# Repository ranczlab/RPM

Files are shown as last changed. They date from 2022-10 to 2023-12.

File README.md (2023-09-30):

# RPM
Documentation files for the Rotation Platform for Mice, as published in Journal of Neuroscience Methods

Read the docs at https://ranczlab.github.io/RPM/

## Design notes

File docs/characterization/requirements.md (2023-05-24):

# Required libraries and software packages

## Software packages
-	[Arduino IDE](https://www.arduino.cc/en/software) 
-	[Teensyduino](https://www.pjrc.com/teensy/teensyduino.html) 

## Required Libraries
-	[Arduino](Arduino/libraries.zip)
-	[ADNS 2160 optical sensor with SQUAL readout](Arduino/libraries.zip) (based on the [OptiMouse library](https://github.com/zapmaker/OptiMouse))
-	[Stepper motor control](https://luni64.github.io/TeensyStep/) 
-	[Encoder](https://github.com/PaulStoffregen/Encoder) 

### Libraries for alternative optical sensors
These are Optical motion sensor options with higher capabilities than the ADNS 2160. All of them use the SPI bus.

-	[ADNS 3500](https://github.com/Tom101222/Adns-3050-Optical-Sensor)
-	[PWM3360](https://github.com/SunjunKim/PMW3360) 
-	[ADNS 9800](https://github.com/mrjohnk/ADNS-9800) 

## Arduino code examples
####[Closed_loop.ino](Arduino/Closed_loop.zip)
The closed loop example uses the optically measured angle increment as a setpoint for the proportional motor control. The animal controls the rotation of the platform.

####[Open_loop.ino](Arduino/Open_loop.zip)
The Open loop example uses two user-defined variables (eg. 0-360 degrees) as setpoints to oscillate between at a user-defined interval.

####[Open_loop_SD.ino](Arduino/Open_loop_SD.zip)
Like the open loop example, but saving the different variables on the SD card on the Teensy 3.5 microcontroller. This program was used to record the accuracy and repeatability measurements.

####[Open_loop_moveAsync.ino](Arduino/Open_loop_moveAsync.zip)
Like Open_loop_SD.ino, but instead of using the proportional control, rotation movement is controlled by the teensystep moveAsync() method, using a non-blocking trapezoidal profile.

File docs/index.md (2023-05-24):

# RPM - a Rotation Platform for head-fixed Mice
## Overview
This device provides vestibular stimulation for head-fixed experiments in mice. It can be combined with different physiological and behavioural recording modalities. It follows a modular, low-cost and open-source model.
This documentation provides the assembly and operation guide for users with some experience in rapid manufacturing, electronics and development boards/microcontrollers, such as Arduino.

In the [accompanying paper](https://www.biorxiv.org/content/10.1101/2023.05.19.541416v1), we show use cases for pupil tracking and recording head-direction cell activity during rotation. 

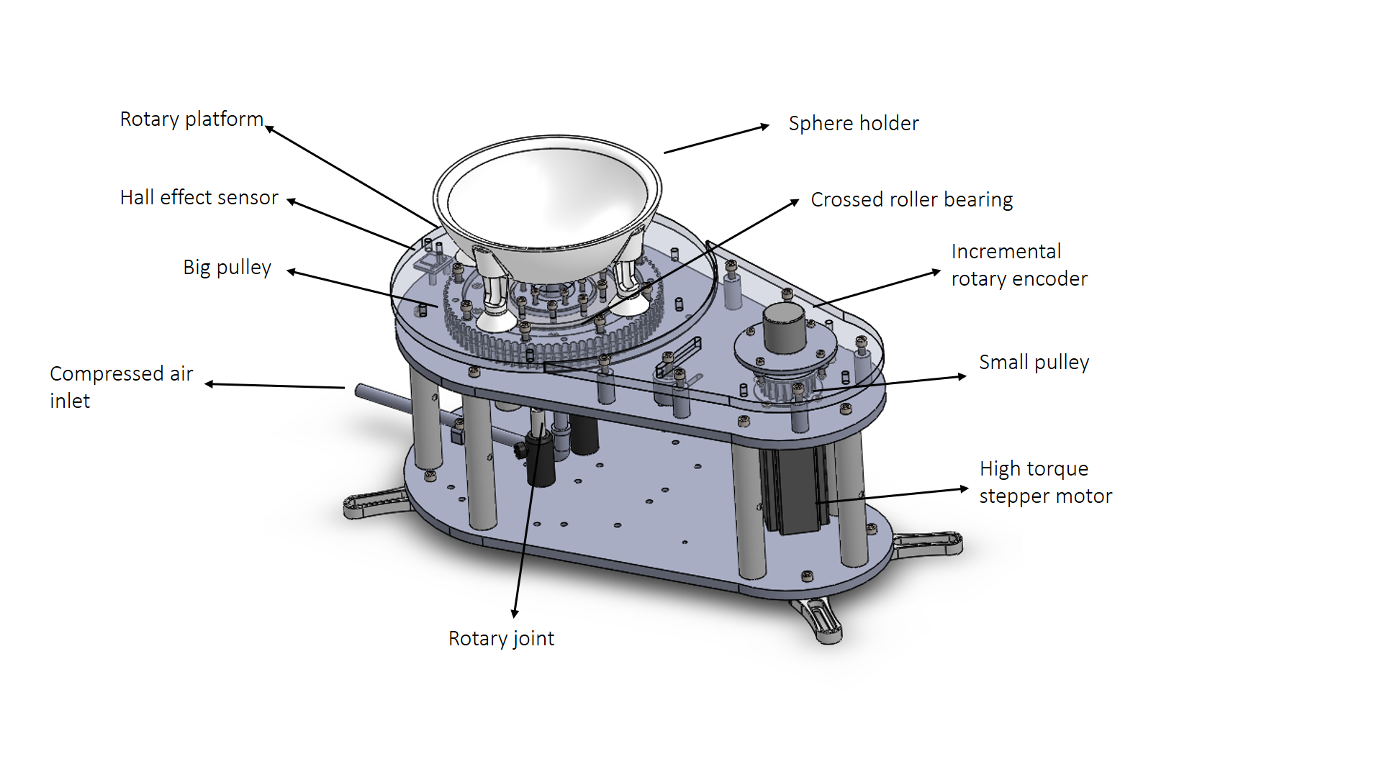
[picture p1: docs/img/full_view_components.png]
|  |
|:--:|
| *Figure 1. Main components of the rotation platform* |
## Features
- fully open source
- low cost
- easy to assemble
- modular design, modules can be added depending on experimental needs

## Main components
The main components of the stage are labelled in the figure above. The rotary platform is actuated by a stepper motor using a timing belt. An incremental encoder is coupled with the motor shaft to measure the angular position, while a Hall effect sensor is used for homing purposes. Compressed air keeps a polystyrene sphere floating without friction inside the sphere holder. The crossed roller bearing holds the rotating and non-rotating parts together. The rotary joint enables multiple electric connections between the rotary platform and the base. The device is intended for behavioural experiments combined with extracellular recording and optogenetics. There are two operating modes: closed-loop and open-loop. In closed-loop mode, the sphere's rotation on the horizontal (yaw) axis is measured using an optical sensor and is used to generate a motor rotation of an adjustable magnitude in the opposite direction. In open-loop mode, motor rotation is independent of the animal’s movement and can be controlled by the experimenter.

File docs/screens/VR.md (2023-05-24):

# Raspberry Pi

The VR environment runs on a Raspberry Pi 4 Modell B located on the platform, running Raspbian 10 (Buster). The Pi is connected to the screens via micro HDMI cables. The Raspberry Pi is powered through one of the USB cables on the slip ring, using a USB to USB-C adaptor. The Teensy USB port is directly connected to one of the USB ports of the Raspberry Pi. Connections are indicated below

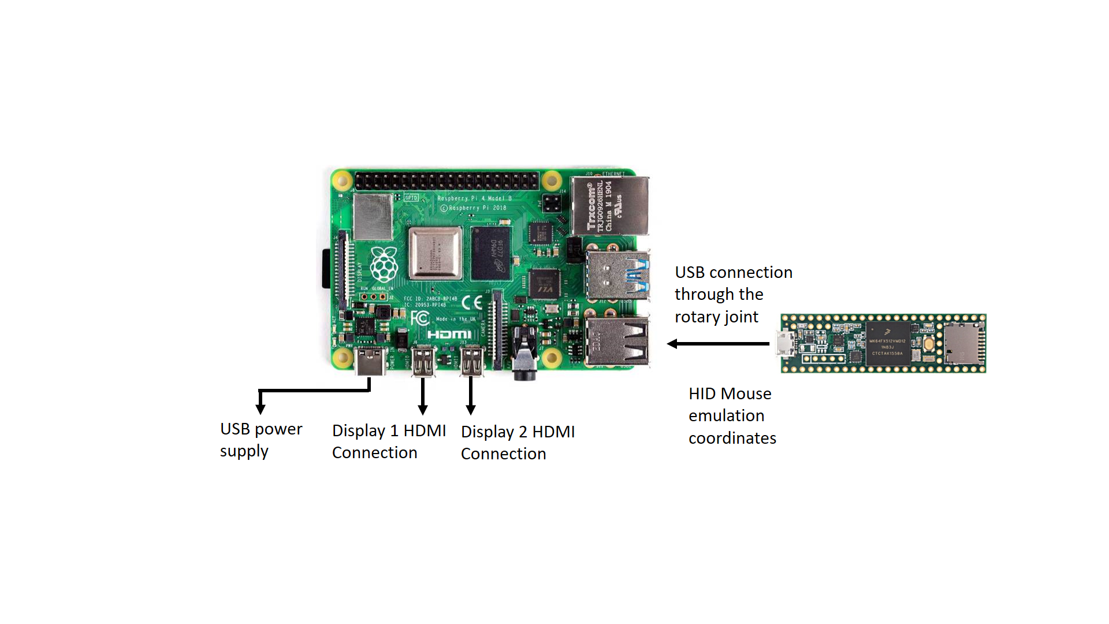
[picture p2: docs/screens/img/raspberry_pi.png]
|  |
|:--:|
| *Figure 1. Connections to Raspberri Pi4* | 
# Sensor input through USB
The optical sensor inputs transformed on the Teensy to calculate the motor displacement are converted using the [Mouse HID Library](https://www.pjrc.com/teensy/td_mouse.html) included in Teensyduino, and transmitted to the Raspberry Pi via USB using the Mouse.move(x, y) function. The Teensy USB port should be set up as a HID + Serial (select the USB mode in Tools -> USB type -> Serial + Keyboard + mouse + joystick when uploading the code using Arduino IDE). 

# Godot

## Compilation instructions
Godot 3.2 is compiled from source using clang. After installing clang and any required libraries (see [here](https://docs.godotengine.org/en/stable/development/compiling/compiling_for_x11.html)), clone and install Godot using the commands below:

```
git clone https://github.com/godotengine/godot
cd godot
git checkout 3.2-stable
scons platform=x11 target=release_debug tools=yes use_llvm=yes CCFLAGS="-mtune=cortex-a72 -mcpu=cortex-a72 -mfloat-abi=hard -mfpu=neon-fp-armv8" -j4
sudo cp bin/godot.x11.opt.tools.32.llvm /usr/bin/godo
```

## Environment

The 3D environment is created in Godot. The camera position is updated using a script written in GDScript, relative to the movements of the emulated mouse carrying the optical sensor input.
The game is run via a bash script that ensures the game is running in full-screen mode across the two monitors.
The (x,y) coordinates of the player within the environment are automatically saved in a csv file. 

The virtual corridor is available [to download here](files/corridor-master.zip)

[The video linked here](https://vimeo.com/829853010) shows a proof-of-principle experiment, where an untrained mouse in navigating on the setup. At the top, a camera behind (and to the right of) the mouse shows the snout, whiskers and the screens. At the bottom, a camera above the setup shows the mouse, the styrofoam ball and the top edge of the screens (helpful to see the physical rotation). The red line in the bottom right shows the trajectory of the animal in VR space.

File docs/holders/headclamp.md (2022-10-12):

## Headplate

The design for the head-plate used with the clamp on the head-holder is shown in Figure 1. 

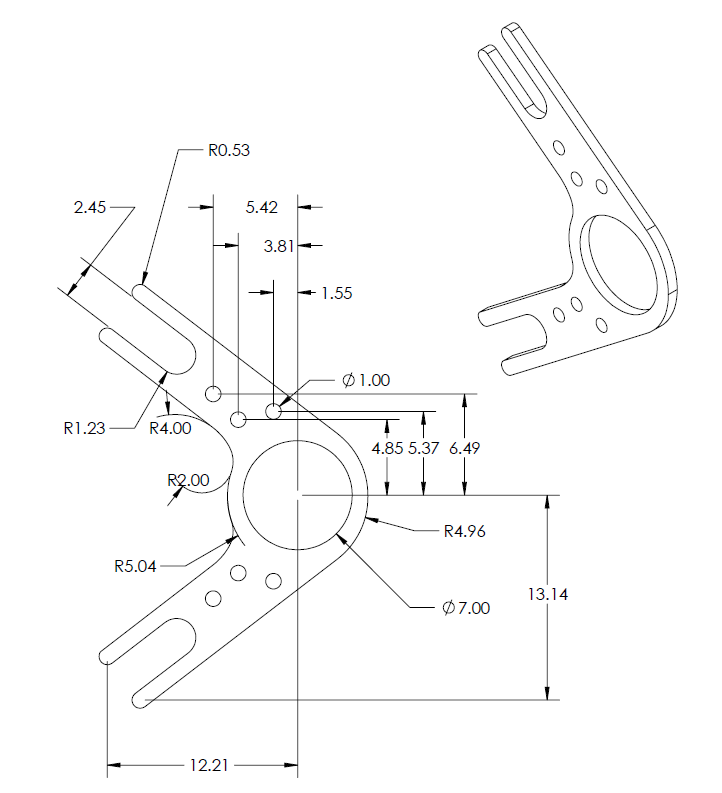
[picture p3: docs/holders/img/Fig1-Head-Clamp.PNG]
|  |
|:--:|
| *Figure 1. Head clamp drawings* |

We have stimulated the performance of the head-plate using different materials (Aluminum, Titanium or Steel) and thicknesses (0.8 mm - 1 mm). The comparison can be performed knowing that the materials will be manufactured using the CNC technique from a block of homogeneous and isotropic material.

The three materials simulated on the Solidworks simulation tool are:

-	Aluminum 6061-T6 1 mm of thickness (0.3g). 
-	Titanium Grade 2 0.8 mm of thickness (0.41g).
-	Stainless steel 316 0.8 mm of thickness (0.73g).

The Initial conditions for the simulation are:

-	A static load applied to the center ring (Blue arrows).
-	Three axis fixture on the parts where the metric 2.5 screws are placed (green arrows).

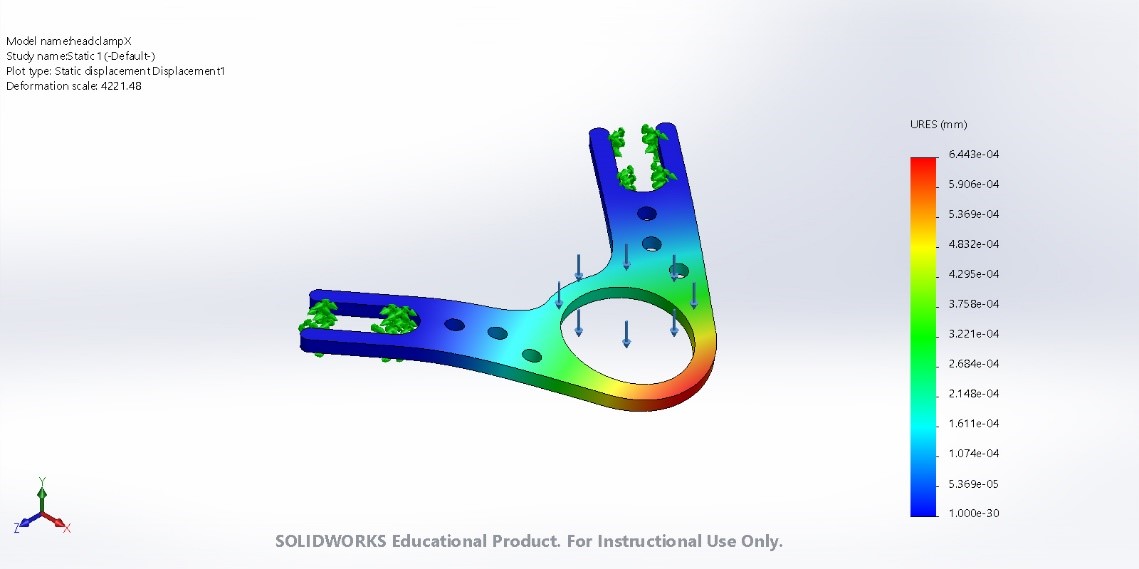
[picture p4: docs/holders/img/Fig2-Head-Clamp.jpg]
|  |
|:--:|
| *Figure 2. Head clamp simulations* |

The results of maximum displacements obtained for each condition

-	Aluminum max. displacement = 9.445e-04 mm
-	Titanium max. displacement = 11.79e-04 mm
-	Stainless Steel max. displacement = 6.443e-04 mm

In conclusion, with the stainless steel head plate of 0.8 mm thickness, the displacement and strain of the head clamp is less than the Aluminum one (1 mm). Otherwise with the Titanium we lose stiffness with 0.8 mm thickness.

Finally, the manufacturing supplier was 3D hubs and the chosen material:

CNC machining / Stainless steel 316L / Smoothed (Ra 1.6μm, 63μin)

The manufacturing files are available [here](files/headclamp/headclampX.IGS) and [here](files/headclamp/headclampX.STL).

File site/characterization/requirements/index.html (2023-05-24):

- Docs »
- Characterization and software »
- Software

# Required libraries and software packages

## Software packages

- Arduino IDE (https://www.arduino.cc/en/software)
- Teensyduino (https://www.pjrc.com/teensy/teensyduino.html)

## Required Libraries

- Arduino
- ADNS 2160 optical sensor with SQUAL readout (based on the OptiMouse library (https://github.com/zapmaker/OptiMouse))
- Stepper motor control (https://luni64.github.io/TeensyStep/)
- Encoder (https://github.com/PaulStoffregen/Encoder)

### Libraries for alternative optical sensors

These are Optical motion sensor options with higher capabilities than the ADNS 2160. All of them use the SPI bus.

- ADNS 3500 (https://github.com/Tom101222/Adns-3050-Optical-Sensor)
- PWM3360 (https://github.com/SunjunKim/PMW3360)
- ADNS 9800 (https://github.com/mrjohnk/ADNS-9800)

## Arduino code examples

#### Closed_loop.ino

The closed loop example uses the optically measured angle increment as a setpoint for the proportional motor control. The animal controls the rotation of the platform.

#### Open_loop.ino

The Open loop example uses two user-defined variables (eg. 0-360 degrees) as setpoints to oscillate between at a user-defined interval.

#### Open_loop_SD.ino

Like the open loop example, but saving the different variables on the SD card on the Teensy 3.5 microcontroller. This program was used to record the accuracy and repeatability measurements.

#### Open_loop_moveAsync.ino

Like Open_loop_SD.ino, but instead of using the proportional control, rotation movement is controlled by the teensystep moveAsync() method, using a non-blocking trapezoidal profile.

Previous

Built with MkDocs (https://www.mkdocs.org/) using a theme (https://github.com/snide/sphinx_rtd_theme) provided by Read the Docs (https://readthedocs.org).

« Previous

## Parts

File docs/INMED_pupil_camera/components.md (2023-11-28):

# Components

Lens
50mm focal length M12 mount lens (CIL051-F2.8-M12ANIR)

M12 Lens extenders
3 x 10 mm per lens 

Camera
FLIR FireFlyS FFY-U3-04S2M-S

## Bill of materials (per screen)
| Component                       | Quantity | Supplier      | Reference                                                  |
|---------------------------------|----------|---------------|------------------------------------------------------------|
| CIL051-F2.8-M12ANIR		 	  | 2       | Commonlands    | [link](https://commonlands.com/products/telephoto-50mm-m12-lens?variant=39733332443254)|
| M12 lens extenders (5 pack)	   	|2         |Amazon|		|[link]https://www.amazon.fr/dp/B0CF9V7S71/ref=pe_27091421_487030221_TE_SCE_3p_dp_1|
| FFY-U3-04S2M-S Camera			|2			|FLIR			|[link]https://www.flir.eu/products/firefly-s/?model=FFY-U3-04S2M-S&vertical=machine+vision&segment=iis|

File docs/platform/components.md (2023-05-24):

# Main components

## Rotary joint

A rotary joint enables electrical communications between the base and the rotating platform. It has a through-hole design for routing the compressed air tube. The selected model is the Senring UH1256-02-0610-06S, of the UH1256-02 Series. It has two USB ports that can be used to connect, e.g. cameras, and several power and data wires to connect different sensors and other accessories.

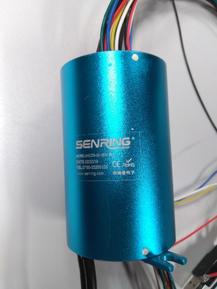
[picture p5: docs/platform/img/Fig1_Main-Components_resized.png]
|  |
|:--:| 
| *Figure 1. Senring UH1256-02-0610-06S Series* |

## Crossed roller bearing

The crossed roller bearing provides a stable joint between the fixed base and the rotation platform. A suitable model for the application is the BRS RU124X considering fitting the rotary joint (inner diameter > 55mm). This bearing provides strong joint stability against axial and radial forces as well as torque due to its best-in-class axial runout (2-5 µm).

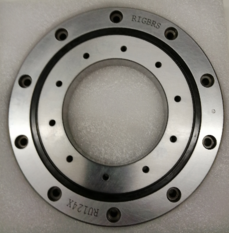
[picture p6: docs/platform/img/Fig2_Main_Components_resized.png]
|  |
|:--:|
| *Figure 2. SBRS RU124X Crossed roller bearing* |

## DC motor and driver
To approximate the motor requirements, we have estimated the moment of inertia around the vertical axis. For this approximation, we have considered two main components: the circular platform and all the elements on the platform and the inner ring of the crossed roller bearing. To simplify the approximation, the internal ring of the bearing has been considered as a stainless steel solid part. The negligible friction force of the bearing has not been taken into account.

Both moments of inertia have been extracted using the mass properties of the Solidworks® CAD software.

equation1

equation2

With this value, we can make the approximation of the torque needed to accelerate the system using Newton’s 2nd law of rotation :
equation3. 

After numerical simulation, we can obtain a theoretical maximum acceleration, useful to choose the motor, described by the function :
equation4

With this relationship, we can estimate the maximum torque needed for the motor. The theoretical maximum angular acceleration is 1100 °/s^2  with a 3 Nm motor option.

A stepper motor was selected accordingly: Nema 23 Stepper Motor 3 Nm 4.2A with a DM542A driver.

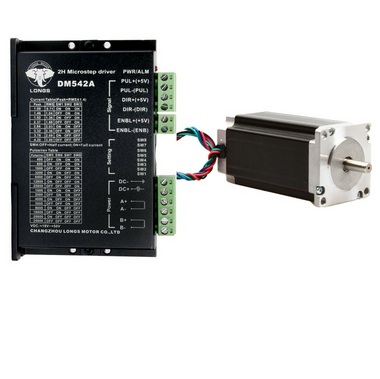
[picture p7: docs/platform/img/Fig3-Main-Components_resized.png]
|  |
|:--:|
| *Figure 3. Nema 23 stepper motor and DM542A stepper driver* |

---
Nema 23 Stepper motor main features:

| Property            	| value 	|
|:---------------------	:|:-------:	|
| steps/rev           	| 200   	|
| L (mH)              	| 3.2   	|
| I<sub>max</sub> (A) 	| 4.2   	|
| V (V)               	| 24    	|
| T (N.m)             	| 3     	|
| P<sub>max</max> (W) 	| 96    	|

---

The current can be selected using the first four switches of the driver DIP switch:
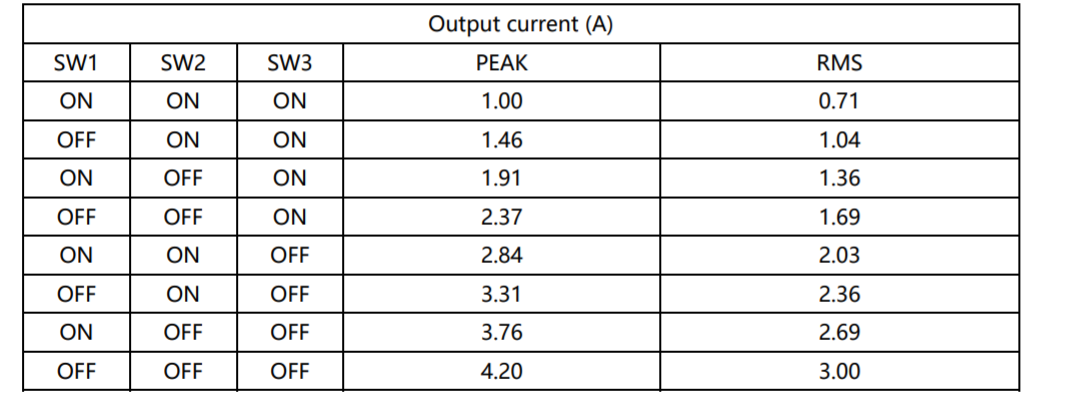
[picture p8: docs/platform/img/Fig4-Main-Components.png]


The driver also has a DIP switch to select the desired micro-stepping mode:
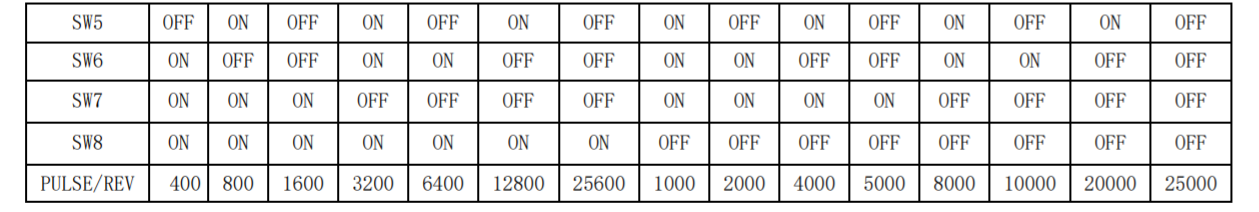
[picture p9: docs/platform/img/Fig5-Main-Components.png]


## Belt selection

We have adjusted the number of teeth zp of the big and the small pulley to get a gear ratio of 6:1 considering the minimum diameter of the big pulley as the outside diameter of the crossed roller bearing BRS RU124X. 

equation11

The diameter of the small (commercially available) pulley with zp = 36 teeth is 34.38 mm. Once the big and small pulley diameters (*D* and *d*) have been defined, the distance between centers (*C*) is calculated to get the desired length *L* :

equation12

The number of teeth obtained for the big pulley is 216, and the distance between centers is 260 mm. These results determined the choice of the belt for our device.
## The timing belt 
The size of the belt was calculated considering the outside diameter of the crossed roller bearing (OD > 165 mm) and the desired gear ratio of 1:6, which provides the stage of a maximum theoretical value of 12 Nm. To calculate the belt parameters, first, we consider the maximum width of the belt for our space constraints, which is 20 mm. According to the distance between centers and the pulley diameters, the required belt length is 927 mm, and the chosen belt width is 15 mm.

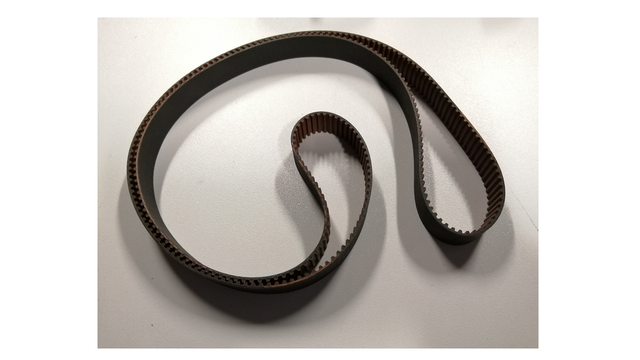
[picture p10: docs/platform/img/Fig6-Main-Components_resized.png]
|  |
|:--:|
| *Figure 6. Timing belt* |

## The small pulley
The pulley driven by the Nema 23 stepper motor is a 36 teeth HTD3 metal pulley provided by RS Components.

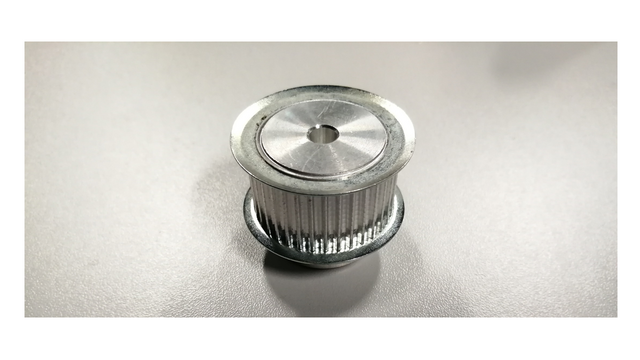
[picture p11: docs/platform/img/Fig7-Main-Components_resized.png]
|  |
|:--:|
| *Figure 7. Small pulley* |

## Bill of materials

3D printing was done using FormLabs Clear V4 resin. PMMA (10 mm thickness) was used for all laser-cut parts unless otherwise indicated.

| Component             	| Quantity 	| Supplier        	| Reference                                                                                                                  |
|-----------------------	|----------	|-----------------	|----------------------------------------------------------------------------------------------------------------------------|
| Resin for 3D printing		|			|					|			|
| Plastic for laser cutting	|			|					|			|
| Base                  	| 1        	| Laser cut		   	| [STEP file](files/STEP/Base.STEP)                                                                                          |
| Platform 2 (Rev1)     	| 1        	| Laser cut 	   	| [STEP file](files/STEP/Platform%202(Rev1).stp)                                                                             |
| Belt cover (Rev1)     	| 1        	| Laser cut 	   	| [STEP file](files/STEP/Belt%20cover(Rev1).stp)                                                                             |
| Circular platform     	| 1        	| Laser cut 	  	| [STEP file](files/STEP/Circular%20rotary%20stage.stp)                                                                      |                                                                                                                                                                                   
| Platform spacer			| 1			| Laser cut			| [STEP file](files/STEP/Spacer.STEP)	|
| Hall-effect sensor spacer | 2         | 3D printed		| [STEP file](files/STEP/Hall%20Effect%20sensor%20spacer.STEP)   															|	
| Hall-effect sensor holder | 1        	| 3D printed 	  	| [STEP file](files/STEP/Hall%20Efect%20sensor%20Holder.stp)                                                                |
| Big pulley (option 1)		| 2			| Laser cut			| [dxf file, layer 1, 5mm thickness](files/dxf/Big pulley%20(1).dxf)|
|							| 1			| Laser cut			| [dxf file, layer 2, 5mm thickness](files/dxf/Big pulley%20(2).dxf)|
|							| 2			| Laser cut			| [dxf file, layer 2, 3mm thickness](files/dxf/Big pulley%20(2).dxf)|
|							| 1			| Laser cut			| [dxf file, layer 3, 3mm thickness](files/dxf/Big pulley%20(3).dxf)|
| Big pulley (option 2, Rev1)     	|         	| 3D printed 	  	| [STEP file](files/STEP/Big%20pulley%20(Rev1).stp), [STL file](files/STL/Big%20pulley%20(Rev1).stl) |                                                                                                                                                                                                        
| Belt tensor           	| 1        	| 3D printed        | [STEP file](files/STEP/Belt%20tensor.STEP) | 
| Encoder holder        	| 1        	| Laser cut 	  	| [STEP file, 5mm thickness](files/STEP/Encoder%20holder.STEP)  |
| Encoder spacer        	| 4        	| Laser cut / 3D printed     | [STEP file, 5mm thickness](files/STEP/Encoder%20spacer.STEP) 	|
| Encoder attachment     	| 1        	| 3D printed      	| [STEP file](files/STEP/Encoder%20attachment.stp), [STL file](files/STL/Encoder%20attachment.stl)     |
| Cover spacer          	| 6        	| 3D printed       	| [STEP file](files/STEP/Cover%20spacer.STEP)  |
| Tube guide            	| 1        	| 3D printed      	| [STEP file](files/STEP/Tube%20guide.STEP)   |
| Rotary joint spacer   	| 1        	| 3D printed     	| [STEP file](files/STEP/Rotary%20joint%20spacer.STEP) |
| Sphere holder   			| 1        	| 3D printed    	| [STL file](files/STL/Sphere%20Holder.STL)       |
| Small pulley (Rev1)   	| 1        	| RS Components 	| [link](https://uk.rs-online.com/web/p/belt-pulleys/1465412/)  |
| Belt                  	| 1        	| Ebay            	| [link](https://www.ebay.co.uk/itm/324243196114)     |
| CF175                 	| 4        	| Thorlabs        	| [link](https://www.thorlabs.com/thorproduct.cfm?partnumber=CF175)    |
| RS05P 				  	| 4        	| Thorlabs        	| [link](https://www.thorlabs.com/thorproduct.cfm?partnumber=RS05P/M)  |
| RS150                 	| 7        	| Thorlabs        	| [link](https://www.thorlabs.com/thorproduct.cfm?partnumber=RS150/M)  |
| TR_50M                	| 2     	| Thorlabs        	| [link](https://www.thorlabs.com/thorproduct.cfm?partnumber=TR50/M)   |
| PH_50                 	| 2        	| Thorlabs        	| [link](https://www.thorlabs.com/thorproduct.cfm?partnumber=PH50/M)    |
| M6 washers            	| 2        	| Thorlabs        	| [link](https://www.thorlabs.com/newgrouppage9.cfm?objectgroup_id=248) |
| M6 screws             	| 44       	| Thorlabs        	| [link](https://www.thorlabs.com/newgrouppage9.cfm?objectgroup_id=248) |
| M5 screws             	| 24       	| Thorlabs        	| [link](https://www.thorlabs.com/newgrouppage9.cfm?objectgroup_id=248) |
| M4 screws             	| 11       	| Thorlabs        	| [link](https://www.thorlabs.com/newgrouppage9.cfm?objectgroup_id=248) |
| M3 screws             	| 7        	| Thorlabs        	| [link](https://www.thorlabs.com/newgrouppage9.cfm?objectgroup_id=248)  |
| M3 grub screw (25mm)		|			| Amazon			| [link](https://www.amazon.co.uk/25mm-Socket-Grub-Screw-Point/dp/B07SJ7XDKB)					|
| M6 nuts               	| 9        	| Thorlabs         	| [link](https://www.thorlabs.com/newgrouppage9.cfm?objectgroup_id=248)  |
| M5 nuts               	| 14       	| Thorlabs       	| [link](https://www.thorlabs.com/newgrouppage9.cfm?objectgroup_id=248)   |
| BRS RU124X bearing    	| 1        	| BRS             	| [link](http://www.rigbrsbearing.com/product/ru124x-cross-roller-ring/)   |
| Rotary Joint          	| 1        	| Senring         	| [link](https://www.senring.com/usb-conductive-slip-ring/dual-Channels/uh1256-02.html)  |
| Encoder               	| 1        	| Amazon          	| [link](https://www.amazon.co.uk/Incremental-Encoder-2-Phases-Photoelectric-Supplies/dp/B085774B2G) |
| Hall effect sensor     	| 1        	| Amazon          	| [link](https://www.amazon.co.uk/AZDelivery-KY-003-Hall-Sensor-Parent/dp/B081B47VM1) |
| Magnet                	| 1        	| RS Components 	| [link](https://uk.rs-online.com/web/p/neodymium-magnets/7924559)  |
| Nema 23 motor & driver 	| 1        	| Ebay            	| [link](https://www.ebay.co.uk/itm/Free-Ship-Nema-23-Stepper-Motor-435oz-in-4-2A-Driver-Controller-DM542A/273805042516) |
| M6 threaded insert    	|          	| RS Components     | [link](https://uk.rs-online.com/web/p/threaded-inserts/6647359)      |
| M4 threaded insert	   	|          	| RS Components   	| [link](https://uk.rs-online.com/web/p/threaded-inserts/0278556)       |
| M3 threaded insert   		|          	| RS Components   	| [link](https://uk.rs-online.com/web/p/threaded-inserts/0278534)     															|
| Bearings              	| 2        	| RS Components 	| [link](https://uk.rs-online.com/web/p/neodymium-magnets/6190014) |
| Pneumatic tube 			| 1			| Amazon			| [link](https://www.amazon.co.uk/ERGAOBOY-Blue-Polyurethane-Pneumatic-Connector/dp/B0BYHPLCDT/)		|
| Pneumatic tube joint		| 1			| Amazon 			| [link](https://www.amazon.co.uk/Pneumatic-Connector-10Pcs-Fittings-Connectors/dp/B095RVTGTG)		|

## Datasheets and documents

| Component             	| Reference                                                                                                                |
|-----------------------	|--------------------------------------------------------------------------------------------------------------------------|
| BRS RU124X bearing	   	| [Datasheet](Datasheets%20and%20documents/Crossed%20roller%20bearing/RU-crossed-roller-bearing-BRS-Bearing.pdf)           |
| 						   	| [Inspection Report](Datasheets%20and%20documents/Crossed%20roller%20bearing/RU124X-Inspection%20Report-BRS Bearing.pdf)  |
| Nema 23 motor & driver 	| [Datasheet](Datasheets%20and%20documents/Motor%20and%20Driver/Nema23_eBay.pdf)		|
| Rotary joint 				| [Datasheet](Datasheets%20and%20documents/Slipring-Rotary%20Joint/Senring-UH1256-01-Series-SlipRing-Catalog.pdf)		|

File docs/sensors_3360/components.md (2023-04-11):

# Components

The PMW3360 has exceptional capabilities: high motion detection for speeds up to 635 cm/s and acceleration up to 50G. The register outputs the SQUAL value, a reference of the quality of the surface. The sensor is available for purchase from JACK Enterprises in Tindie [[1]](#references). To control it you must download the PWM3360 library [[2]](#references). 

The breakout board has the essential pins available and distributed in a way that makes it easy to connect:

- VI = 3.3V
- MI = MISO0 -or- DIN
- MO = MOSI0 -or- DOUT
- SC = SCK0 -or- SCK
- SS = CS0 -or- CS
- GD = GND

The holder can be 3D printed ([STL file](files/STL/PWM3360%20holder.stl) and [STP file](files/STP/PWM3360%20holder.stp)) and be used with the Thorlabs parts described for the other sensors (ADNS 2610 and 3050). To attach the sensor to the holder, two M2.5 16 mm pan head screws and two M2.5 nuts are needed. The nuts can be pressed to fit on the holder, and the bolts will hold the lens against the sensor without needing glue (Figure 1).

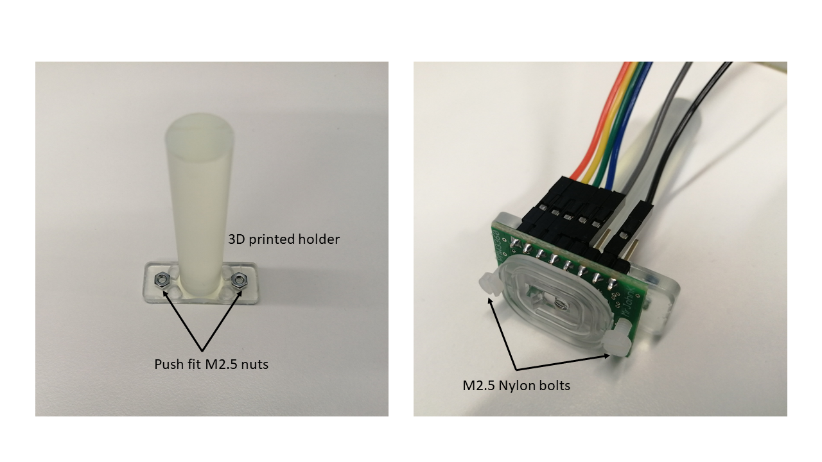
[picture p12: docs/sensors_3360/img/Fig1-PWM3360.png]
|  |
|:--:|
| *Figure 1. 3D printed holder and assembly* |

# References
[1] [https://www.tindie.com/products/jkicklighter/pmw3360-motion-sensor/](https://www.tindie.com/products/jkicklighter/pmw3360-motion-sensor/)

[2] [https://github.com/SunjunKim/PMW3360](https://github.com/SunjunKim/PMW3360)

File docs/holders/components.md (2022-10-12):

## Instrument ring

A ring-shaped instrument platform can be mounted around the sphere to hold several devices, such as an animal head-holder, cameras, and manipulators for electrical recording and optogenetic stimulation. Below we present options for head-clamps and holders for manipulating recording probes or optical fibres.

|  |
|:--:|
| *Figure 1. Ring platform and head holding system* |

## Head-plate holder

We designed a head fixation system with three degrees of freedom. The height of the head-plate holder can be adjusted to accommodate mice of different sizes. In addition, two orthogonal axes are used in the horizontal plane to adjust the position of the animal's head. This is particularly useful for vestibular experiments to centre the platform rotation axis on the vestibular organ of interest. 

This head holding system is based on assembling 3 manual Thorlabs translational stages (MT1\M) to ensure reliability and repeatability across experiments. The resolution of the system is 10 microns with a range of 13 mm in all directions.

|  |
|:--:|
| *Figure 2. Virtual assembly of the head post (left) and real assembly (right).* |

The materials needed for the assembly are: 3D printable parts (MT1/M linker, Head plate holder 1), the three MT1\M translational stages, three MT405 side mounted actuator adapters, two M2.5 nuts, two hexagonal M2.5 screws, fifteen M6 screws (two of them optional) and two M6 threaded inserts (optional). 

|  |
|:--:|
| *Figure 3. Drawings of the MT1/M linker at 1:2 scale* |

We also provide an MT1/M linker with a side-lip useable for attaching e.g. a camera or another instrument. 
An alternative Head-plate holder 2 is provided for attaching an MM33 manual micromanipulator. 

## Probe holder and optic fibre holder

A probe holder is provided for attaching e.g. a Neuronexus adaptor (Adpt-A32-OM32) to the MM33 micromanipulator for electrophysiological recordings.

For optogenetic stimulation, an optic fibre can be secured to the MM33 micromanipulator using the Thorlabs FCM13/M ferrule clamp and a custom 3D printed adaptor. This allows the positioning of the light source at the desired location over the animal's head.

|  |
|:--:|
| *Figure 6. Optical fiber holder* |

## Bill of materials
The 3D printed parts have been printed using a Form2 SLS 3D printer using the default settings with Clear V4 resin type.

| Component                           | Manufacturer    | Units           | Reference             |
|-------------------------------------|-----------------|-----------------|-----------------------|
| Instrument ring                     | 3D printed 		| 1               | [STP file](files/STEP/Ring.stp), [STL files](files/STL/Ring.stl)        |
| MT1/M linker						  | 3D printed 		| 1               | [STP file](files/STEP/linkMT1_M.stp)|
| MT1/M linker with camera holder lip | 3D printed 		| 1               | [STP file](files/STEP/linkMT1_M_camera%20modification.STEP), [STL files](files/STL/linkMT1_M_camera%20modification.STL)        |
| Head-plate holder 1				  | 3D printed		| 1				  |	[STP file](files/STEP/Head_plate_holder_1.stp)				|
| Head-plate holder 2 (for MM33 manipulator)            | 3D printed	  | 1               | [STP file](files/STEP/Head_plate_holder_2.stp), [STL file](files/STL/Head_plate_holder_2.stl)        |
| Probe holder                  	  | 3D printed 		| 1               | [STP file](files/STEP/Neuronexus%20holder.stp) |
| Optic fiber holder                  | 3D printed 		| 1               | [STP file](files/STEP/Optic%20fiber%20holder.stp), [STL file](files/STL/Optic%20fiber%20holder.stl) |
| MT1/M translational stage           | Thorlabs        | 3               | [link](https://www.thorlabs.com/thorproduct.cfm?partnumber=MT1/M#ad-image-0)                 |
| MT405 side mounted actuator adapter | Thorlabs        | 3               | [link](https://www.thorlabs.com/newgrouppage9.cfm?objectgroup_id=1908&pn=MT405#1929)                 |
| RS6P/M posts						  | Thorlabs		| 2				  | [link](https://www.thorlabs.com/newgrouppage9.cfm?objectgroup_id=851&pn=RS6P/M#1307)|
| M6 hex bold screws 16mm length      | RS components   | 15 (2 optional) | [link](https://uk.rs-online.com/web/p/socket-screws/0281114)               |
| M2.5 hex bold screws                | RS components   | 4               | [link](https://uk.rs-online.com/web/p/socket-screws/4838124)      |
| M2.5 nuts                           | RS components   | 2               | [link](https://uk.rs-online.com/web/p/hex-nuts/0560287)               |
| M6 threaded inserts                 | RS components   | 2 (optional)    | [link](https://uk.rs-online.com/web/p/threaded-inserts/6647359)              |
| M4 screws                           |                 | 3               |                       |
| M3 screws                           |                 | 2               |                       |
| Optic fibre holder (FCM ferrule clamp)				  | Thorlabs		| 1				  | [link](https://www.thorlabs.com/newgrouppage9.cfm?objectgroup_id=69)
| Left handed MM33 micromanipulator   | Märzhäuser      | 1               |[link](https://www.marzhauser.com/en/products/micromanipulators/manual-micromanipulators/mm-33.html), [datasheet](files/Datasheets/Micromanipulator/00-42-101-0000_MM_33_EN.pdf)|

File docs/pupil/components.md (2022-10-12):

# Camera-mirror complex for pupil tracking

A camera can be added to the ring-shaped instrument platform to record e.g. eye or facial movements. We chose a web camera with a small footprint, low weight and USB connectivity through the rotary joint. It lacks an IR filter. We used an IR LED for illumination and a Thorlabs FEL0750 - Ø1" long pass filter mounted on a CP35/M - 30 mm cage Plate using an SM1L03 lens tube. 

The image of the animal is reflected on an FM02R red hot mirror ((25 mm x 36 mm) with an incidence angle of 45°. The mirror position can be adjusted with Thorlabs post elements, and the camera can be rotated and translated for adequate positioning.

|  |
|:--:|
| *Figure 1. Camera with hot mirror* | 

## Bill of materials

| Component                            	| Quantity 	| Supplier 	| Reference                                                                                      	|
|--------------------------------------	|----------	|----------	|------------------------------------------------------------------------------------------------	|
| Mirror holder                        	| 1        	| 3D   printed        	|[STP file](files/STEP/Mirror%20holder.STEP), [STL file](files/STL/Mirror%20holder.STL)                                                                              	|
| Camera holder                        	| 1        	| 3D   printed        	|[STP file](files/STEP/Camera%20holder.STEP), [STL file](files/STL/Camera%20holder.STL)                                                                              	|
| Filter holder                        	| 1        	| 3D   printed        	|[STP file](files/STEP/Filter%20holder.STEP), [STL file](files/STL/Filter%20holder.STL)                                                                              	|
| Filter holder cover                  	| 1        	| 3D   printed        	|[STP file](files/STEP/Filter%20holder%20cover.STEP), [STL file](files/STL/Filter%20holder%20cover.STL)                                                                              	|
| M2 screw                             	| 4        	| -        	| -                                                                                              	|
| M3 screw                             	| 6        	| -        	| -                                                                                              	|
| M2 nuts                              	| 4        	| -        	| -                                                                                              	|
| M6 screw                             	| 1        	| -        	| -                                                                                              	|
| M6 nut                               	| 1        	| -        	| -                                                                                              	|
| FEL0750 - Ø1" Long pass Filter       	| 1        	| Thorlabs 	| [link](https://www.thorlabs.de/thorproduct.cfm?partnumber=FEL0750)                                     	|
| CP35/M - 30 mm Cage Plate            	| 1        	| Thorlabs 	| [link](https://www.thorlabs.com/thorproduct.cfm?partnumber=CP35/M)                                     	|
| SM1L03 - SM1 Lens Tube               	| 1        	| Thorlabs 	| [link](https://www.thorlabs.com/thorproduct.cfm?partnumber=SM1L03)                                     	|
| FM02R - 25 mm x 36 mm Red Hot Mirror 	| 1        	| Thorlabs 	| [link](https://www.thorlabs.com/thorproduct.cfm?partnumber=FM02R)                                      	|
| ELP webcam 				         	| 1        	| Amazon   	| [link](https://www.amazon.co.uk/gp/product/B015PCAVZG) 	|

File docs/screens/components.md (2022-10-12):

# Components

Two 8” SKD819VAHT-9 TFT displays are attached to the rotary platform using two Thorlabs RS6P_M posts. The displays are attached to the posts with a 3D printed part (Screen attachment 1). The display frame comprises three laser-cut acrylic parts and some laser-cut spacers. Eight M4 screws and nuts are required to build the acrylic structure, and an M6 screw is required to attach the 3D printed attachment with the Thorlabs post.

## Bill of materials (per screen)
| Component                       | Quantity | Supplier      | Reference                                                  |
|---------------------------------|----------|---------------|------------------------------------------------------------|
| SKD819VAHT-9 TFT screens		  | 1        | -             | [link](https://www.alibaba.com/product-detail/SKD819VAHT-9-HDMI-Input-Touch-screen_1600192797730.html)                                               |
| Screen holder front             | 1        | Laser cut              | [STP file](files/STEP/Screen%20holder%20front.stp), [DXF file](files/DXF/Screen%20holder%20front.dxf)                                             |
| Screen holder back              | 1        | Laser cut              | [STP file](files/STEP/Screen%20holder%20Back.stp), [DXF file](files/DXF/Screen%20holder%20back.dxf)                                             |
| Screen holder back 2            | 1        | Laser cut              | [STP file](files/STEP/Screen%20holder%20Back%202.stp), [DXF file](files/DXF/Screen%20holder%20back%202.dxf)                                             |
| Screen attachment 1             | 1        | 3D printed              | [STP file](files/STEP/Screen%20attachment%201.stp), [STL file](files/STL/Screen%20attachment%201.stl)                                            |
| Spacer                          | 4        | 3D printed              | [STP file](files/STEP/Spacer.stp), [STL file](files/STL/Spacer.stl)                                            |
| Spacer 2                        | 4        | 3D printed              | [STP file](files/STEP/Spacer%202.stp), [STL file](files/STL/Spacer%202.stl)                                            |
| RS6P/M                          | 1        | Thorlabs      | [link](https://www.thorlabs.com/thorproduct.cfm?partnumber=RS6P/M) |
| M4 screw                        | 8        | RS Components | [link](https://uk.rs-online.com/web/p/socket-screws/0281057/)      |
| M4 nut                          | 4        | RS Components | [link](https://uk.rs-online.com/web/p/hex-nuts/0189579/)           |
| M6 screw                        | 1        | RS Components | [link](https://uk.rs-online.com/web/p/socket-screws/8741030/)      |

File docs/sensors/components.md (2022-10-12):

# Optical motion sensors

## Sensors

To measure the position of the sphere, we used two PCB boards based on the Avago Technologies ADNS-2610 [[1]](#references) optical flow sensor and extracted from the Logitech M-SBF96 PS2 computer mouse. This sensor presents high reliability for speeds under 30.5 cm/s, and has a register that outputs the SQUAL value, a reference for the quality of the surface. This SQUAL value can be used for calibration and optimization. 

|  |
|:--:|
| *Figure 1. Pinout of the ADNS-2610* |

The PCB and lens are attached to a 3D printable structure and assembled with 3 Thorlabs components.

|  |
|:--:|
| *Figure 2. Optical sensor* |

## Bill of materials (per sensor)

The 3D-printed parts have been designed to be printed optimally with an Objet 30 (Polyjet resin printer), but have also been printed with a Form 2 (SLS resin printer). We used the Vero gray resin and the Clear V4 resin with the Objet 30 and the Form 2 respectively. Printer settings were kept at default.

| Component          | Quantity | Supplier      | Reference                                                                                               |
|--------------------|----------|---------------|-----------------------------------------------------------------------------------------------------------|
| Optical mouse      | 1        | -             | [example link](https://www.ebay.com/itm/232746871340) |
| Sensor holder      | 1        | 3D printed    | [STEP file](files/Sensor%20holder.stp), [STL file](files/Sensor%20holder.stl)                            |
| PH75/M             | 1        | Thorlabs      | [link](https://www.thorlabs.com/thorproduct.cfm?partnumber=PH75/M)                                           |
| RA180/M            | 1        | Thorlabs      | [link](https://www.thorlabs.com/newgrouppage9.cfm?objectgroup_id=1985&pn=RA180#6066)                        |
| TR75V/M            | 1        | Thorlabs      | [link](https://www.thorlabs.com/newgrouppage9.cfm?objectgroup_id=1266&pn=TR75V/M#7832)               |
| M3 x 6 mm          | 2        | RS Components | [link](https://uk.rs-online.com/web/p/grub-screws/0137720)                                             |
| M3 threaded insert | 2        | RS Components | [link](https://uk.rs-online.com/web/p/threaded-inserts/0278534)                                       |

# References

[1] [ADNS-2610 datasheet](datasheets/ADNS-2610.pdf)

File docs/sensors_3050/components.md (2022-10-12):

# Optical motion sensors - option 2, ADNS-3050

## Sensors

Another option to measure the sphere's position is to use two PCB boards based on the Avago Technologies ADNS-3050 optical flow sensor. The sensor was extracted from the Cougar Minos X2 gaming computer mouse. This sensor has high motion detection under speeds of 152.4 cm/s and can deal with accelerations up to 20G. It has selectable resolutions up to 2000 cpi (we have used the default configuration of 1000 cpi). Furthermore, the register outputs the SQUAL value, which is used for the calibration and adjustment process.

|  |
|:--:|
| *Figure 1. Pinout of the ADNS-3050* |

## Bill of materials (per sensor)
| Component          | Quantity | Supplier      | Reference                                                                                                                                               |
|--------------------|----------|---------------|---------------------------------------------------------------------------------------------------------------------------------------------------------|
| Optical mouse      | 1        | -             | [link](https://cougargaming.com/products/mice/minos_x2/)|
| PCB Holder 1     | 1        | 3D printed part             | [STEP file](files/STEP/PCB%20holder.STEP), [STL file](files/STL/PCB%20holder.STL) |
| PCB Holder 2    | 1        | 3D printed part             | [STEP file](files/STEP/PCB%20holder%202.STEP), [STL file](files/STL/PCB%20holder%202.STL) |
| M3 screws       | 4        | RS Components               |                                                                             |

The rest of the components are the same as described in the ADNS 2610 assembly.

# Datasheets
[1] [ADNS-3050 datasheet](datasheets/adns-3050.pdf)

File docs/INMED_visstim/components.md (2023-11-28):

# Components

Visual stimuli used for experiments 

1. Motion Clouds 
Based on [link]https://neuralensemble.org/MotionClouds/index.html

## Bill of materials (per screen)
| Component                       | Quantity | Supplier      | Reference                                                  |
|---------------------------------|----------|---------------|------------------------------------------------------------|
| example		 				  | 1        | -             | [link](https://www.alibaba.com/product-detail/SKD819VAHT-9-HDMI-Input-Touch-screen_1600192797730.html)

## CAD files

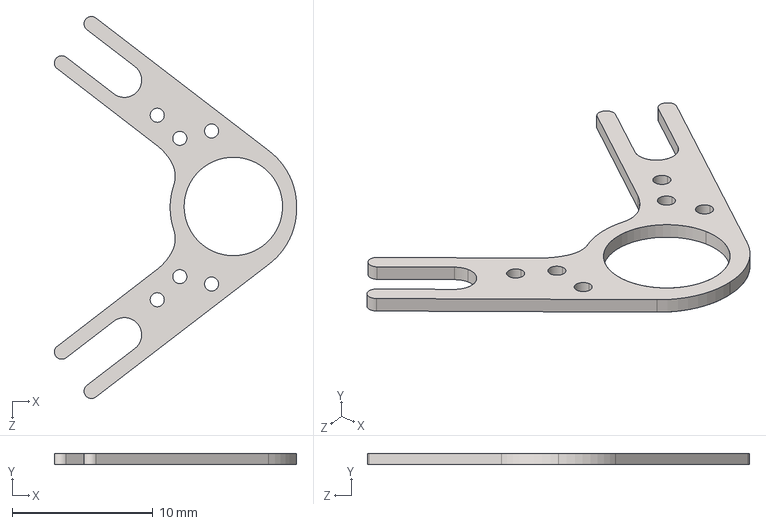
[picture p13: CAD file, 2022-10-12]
docs/holders/files/headclamp/headclampX.IGS
17.2 x 0.8 x 27.2 mm

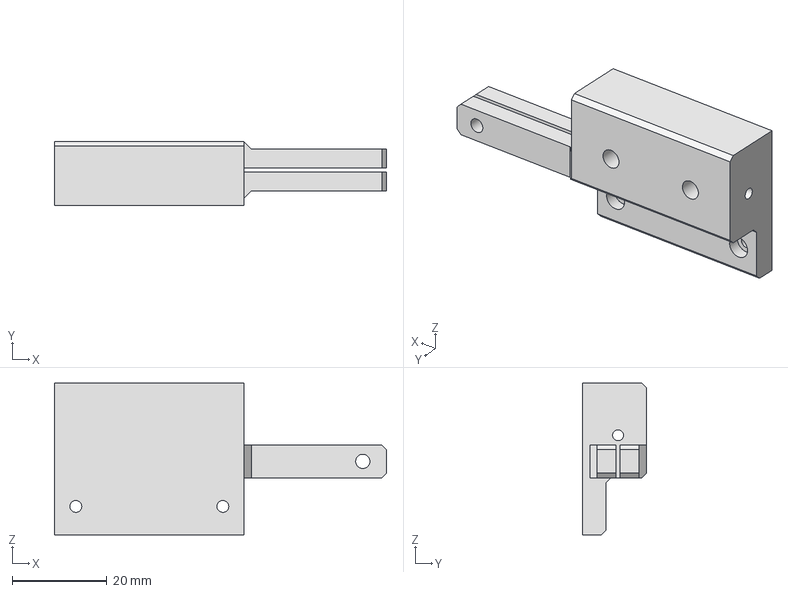
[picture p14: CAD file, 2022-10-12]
docs/holders/files/STEP/Neuronexus holder.stp
70.0 x 13.5 x 32.0 mm

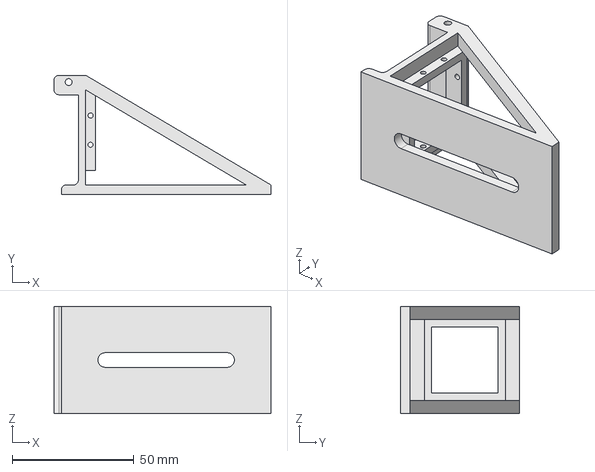
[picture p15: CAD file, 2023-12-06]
docs/INMED_camera_holder/STEP/camera_holder_new.step
89.0 x 49.0 x 44.0 mm

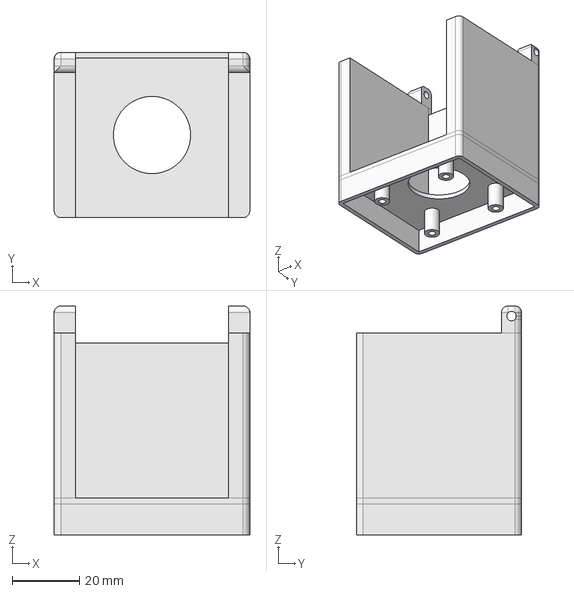
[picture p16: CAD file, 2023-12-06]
docs/INMED_filter_holder/STEP/filter_holder_new.step
58.0 x 49.0 x 67.9 mm

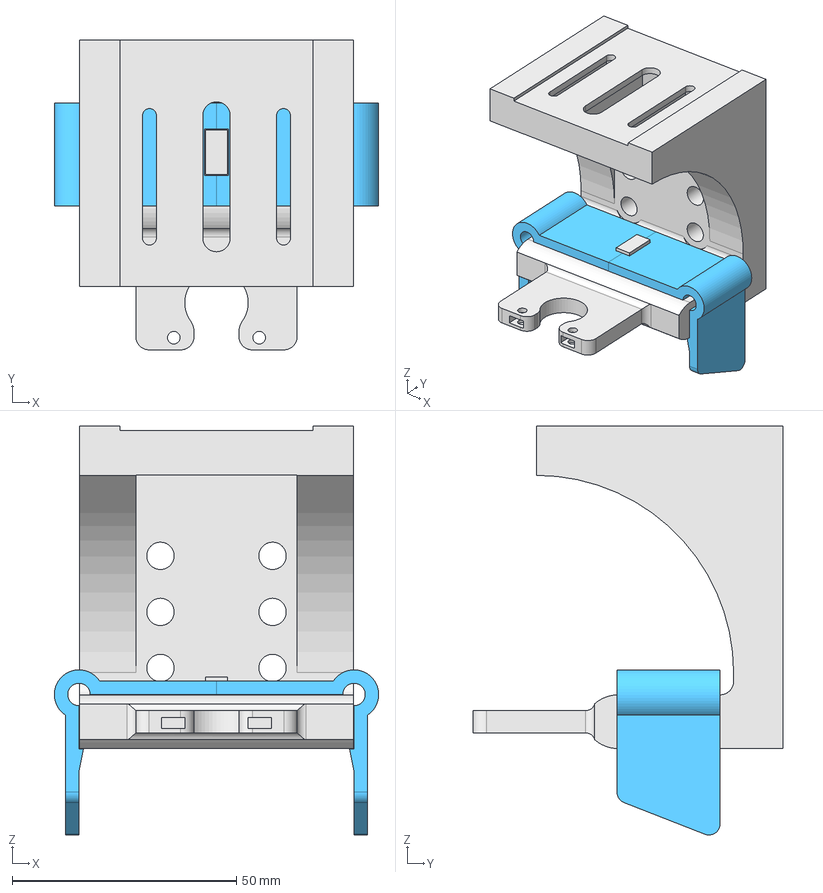
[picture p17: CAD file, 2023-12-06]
docs/INMED_headholder/FreeCAD/dtb12-linker.FCStd
72.3 x 69.1 x 91.2 mm
dtb12-linker
ears-3dp

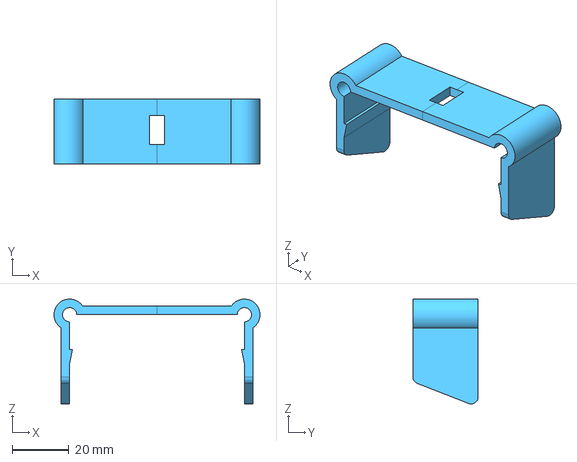
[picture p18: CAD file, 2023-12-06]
docs/INMED_headholder/STEP/ears.step
72.3 x 23.0 x 36.8 mm

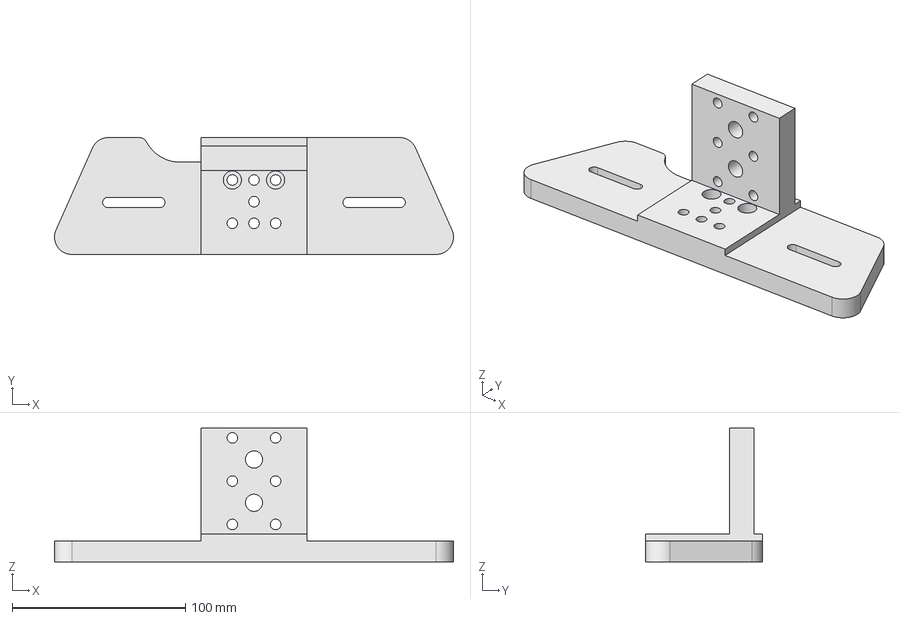
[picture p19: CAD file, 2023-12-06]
docs/INMED_linkMT1_modified/STEP/MT1L_linker.step
230.4 x 67.5 x 77.2 mm

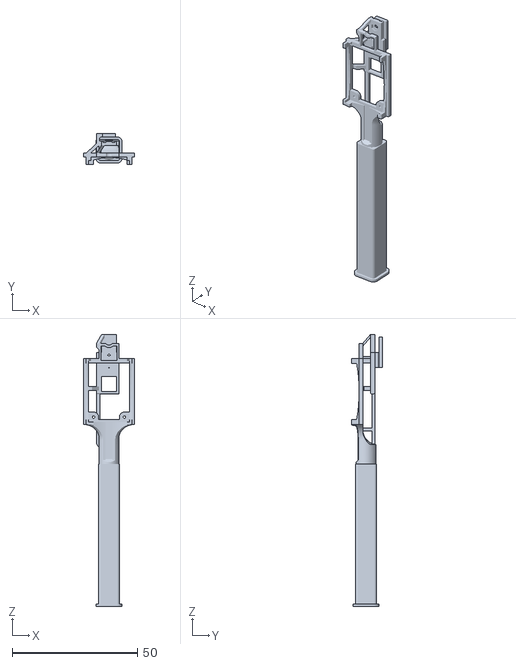
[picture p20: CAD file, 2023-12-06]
docs/INMED_NPX_holder/STL/npx_holder.stl
20.3 x 12.3 x 108.8

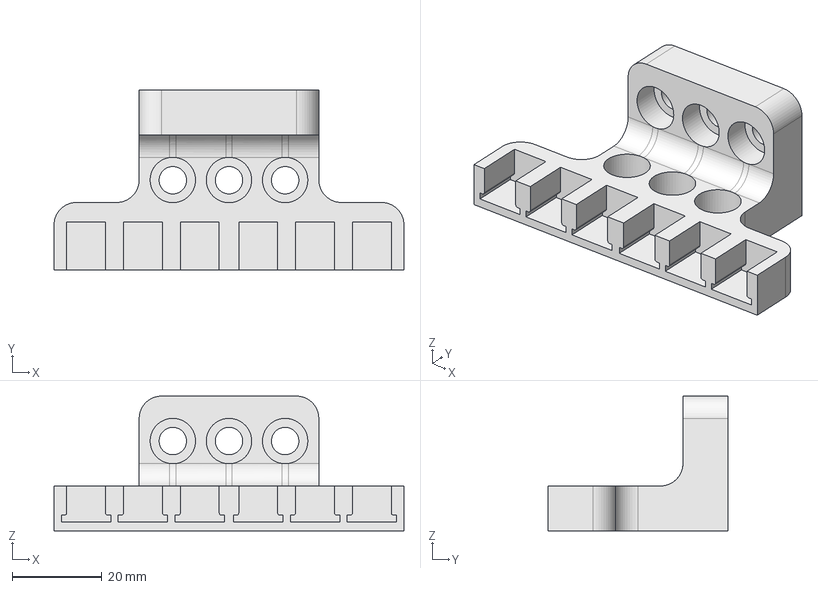
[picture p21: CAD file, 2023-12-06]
docs/INMED_npx_holder_holder/STEP/npx-holder-holder.step
77.9 x 40.0 x 30.0 mm

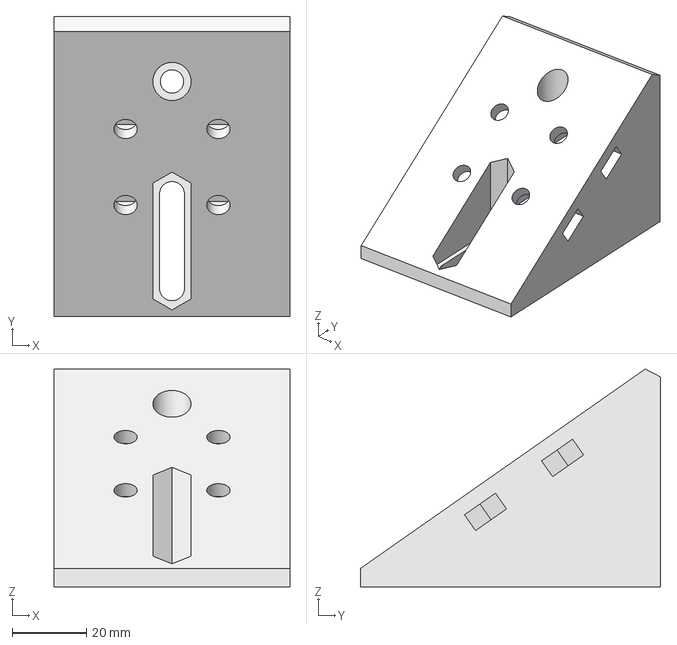
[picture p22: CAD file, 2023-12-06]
docs/INMED_NPX_scope_assembly/STEP/NPX_scope_holder.step
63.5 x 80.8 x 58.7 mm

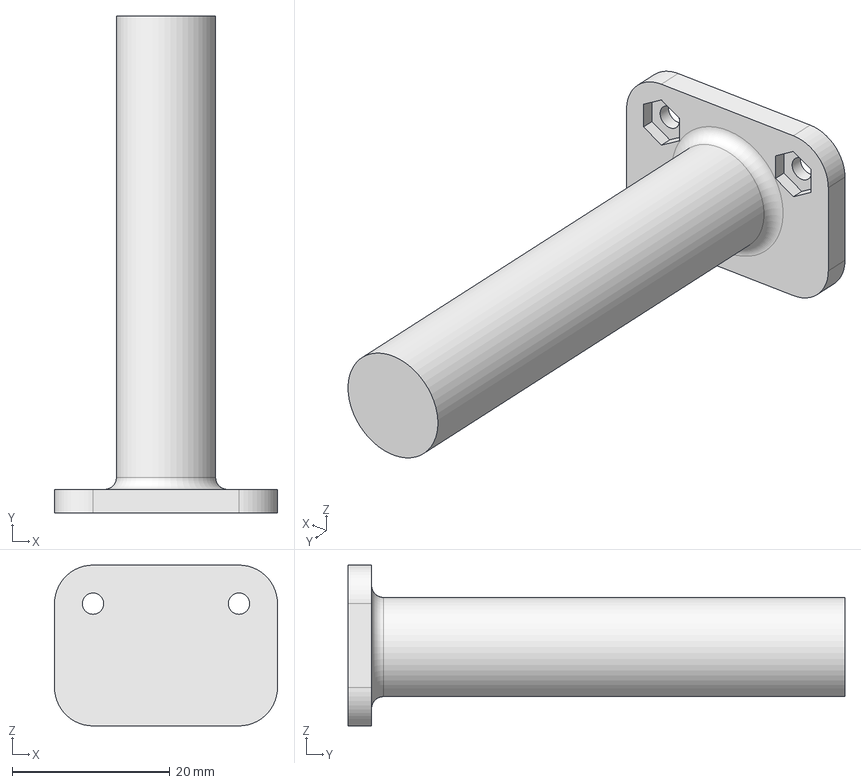
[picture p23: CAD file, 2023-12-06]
docs/INMED_optic_sensor_holder_new/STEP/optic-sens-holder.step
28.3 x 63.0 x 20.4 mm

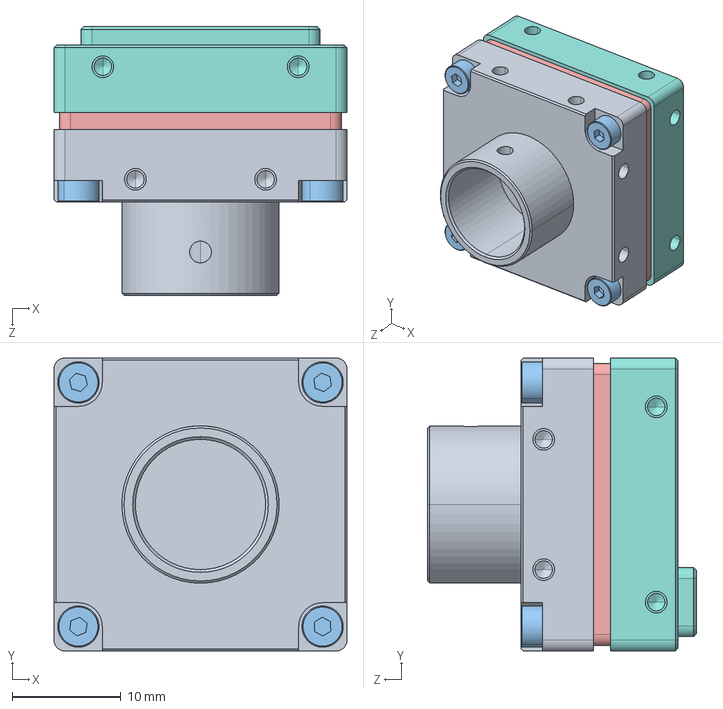
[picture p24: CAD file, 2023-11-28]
docs/INMED_pupil_camera/files/STP/FFY-U3-50-R1.STEP
27.0 x 27.0 x 24.8 mm

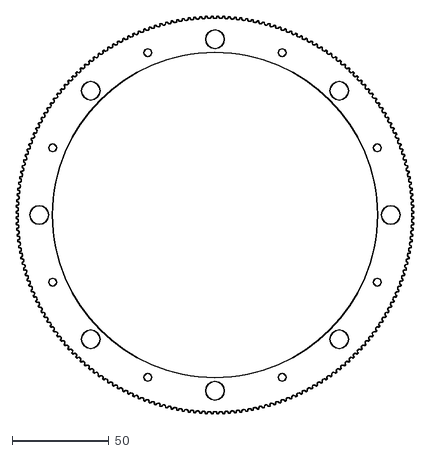
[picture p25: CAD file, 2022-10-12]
docs/platform/files/dxf/Big pulley (3).dxf
205.5 x 205.5

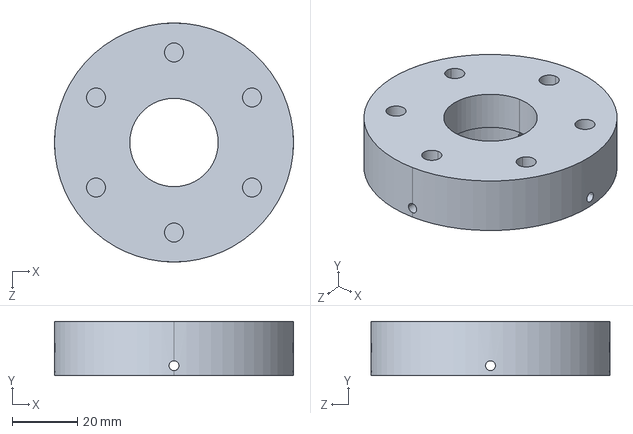
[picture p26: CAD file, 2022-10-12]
docs/platform/files/STEP/Rotary joint spacer.STEP
73.0 x 16.5 x 73.0 mm

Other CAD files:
docs/pupil/files/STEP/Mirror holder.STEP
docs/screens/files/STEP/RS6P_M.stp
docs/sensors/files/Sensor.STEP
docs/sensors_3050/files/STEP/PCB holder.STEP
docs/INMED_NPX_scope_assembly/FreeCAD/NPX_scope_holder.FCStd
docs/INMED_NPX_scope_assembly/STL/NPX_scope_holder.stl
docs/INMED_Newscale-Thorlabs_assembly/STEP/adapt1.step
docs/INMED_Newscale-Thorlabs_assembly/STEP/adapt2.1.step
docs/INMED_Newscale-Thorlabs_assembly/STEP/adapt2.2.step
docs/INMED_Newscale-Thorlabs_assembly/STL/adapt1.stl
docs/INMED_Newscale-Thorlabs_assembly/STL/adapt2.1.stl
docs/INMED_Newscale-Thorlabs_assembly/STL/adapt2.2.stl
docs/INMED_camera_holder/FreeCAD/camera_holder_new.FCStd
docs/INMED_camera_holder/STL/camera_holder_new.stl
docs/INMED_filter_holder/FreeCAD/filter_holder_new.FCStd
docs/INMED_filter_holder/STL/filter_holder_new.stl
docs/INMED_headholder/STEP/headholder_new.step
docs/INMED_headholder/STL/ears.stl
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

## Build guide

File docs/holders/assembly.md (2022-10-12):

# Assembly

We show an example assembly using the MT1/M linker with camera holder lip, the Head-plate holder 2, the MM33 micromanipulator and the probe holder. 

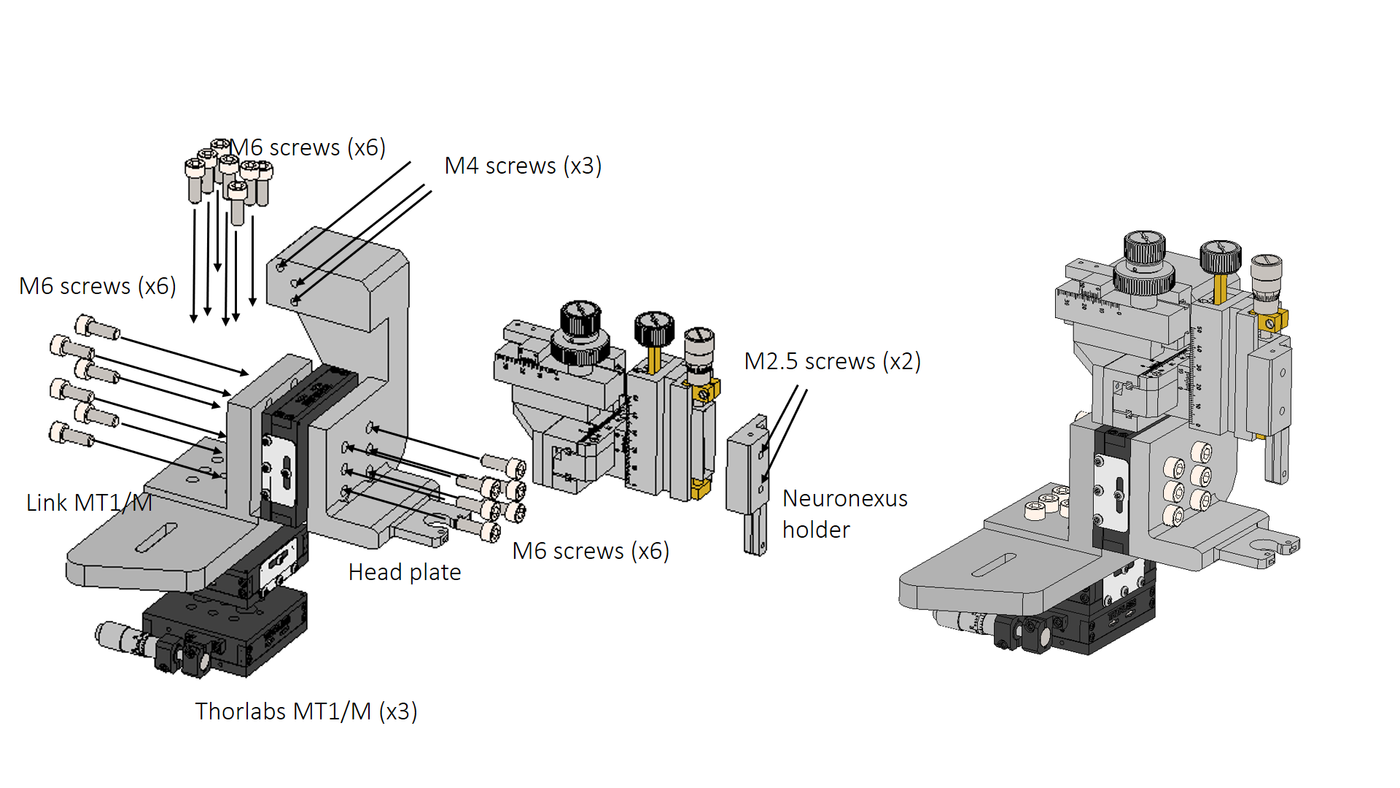
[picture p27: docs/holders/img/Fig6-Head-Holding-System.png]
|  |
|:--:|
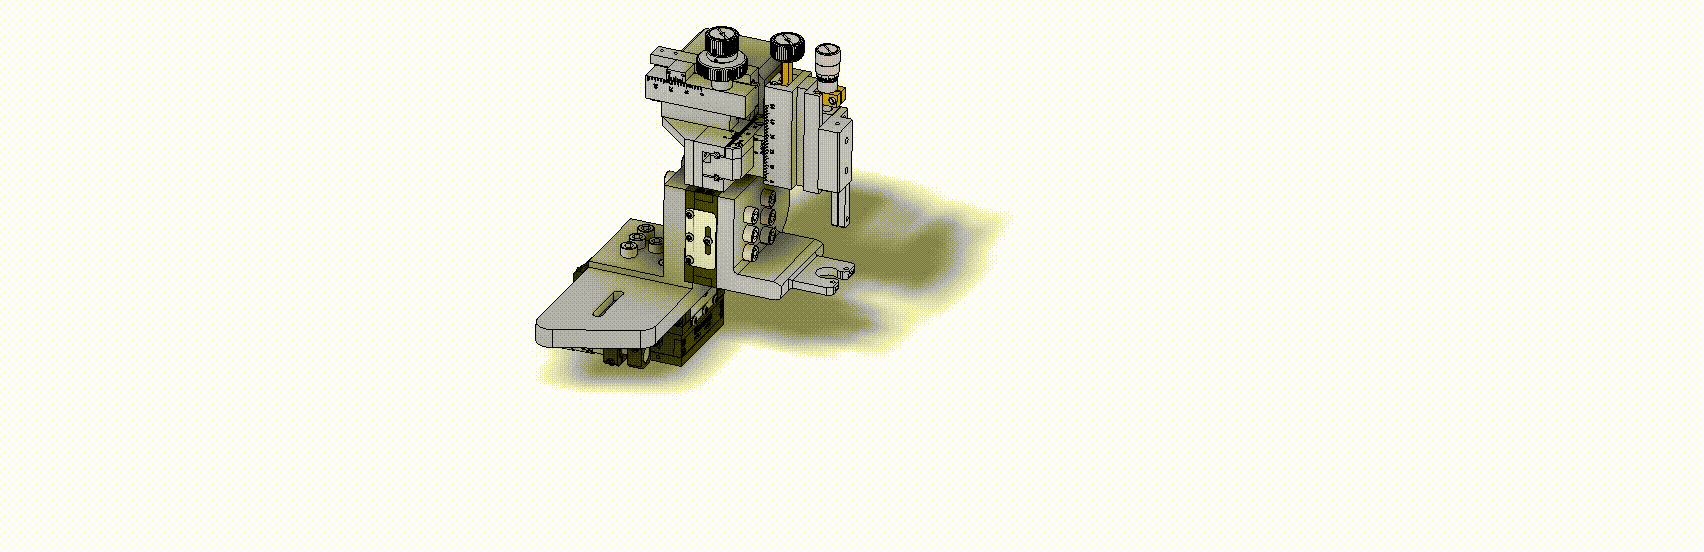
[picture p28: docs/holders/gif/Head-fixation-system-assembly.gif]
|  |
|:--:|
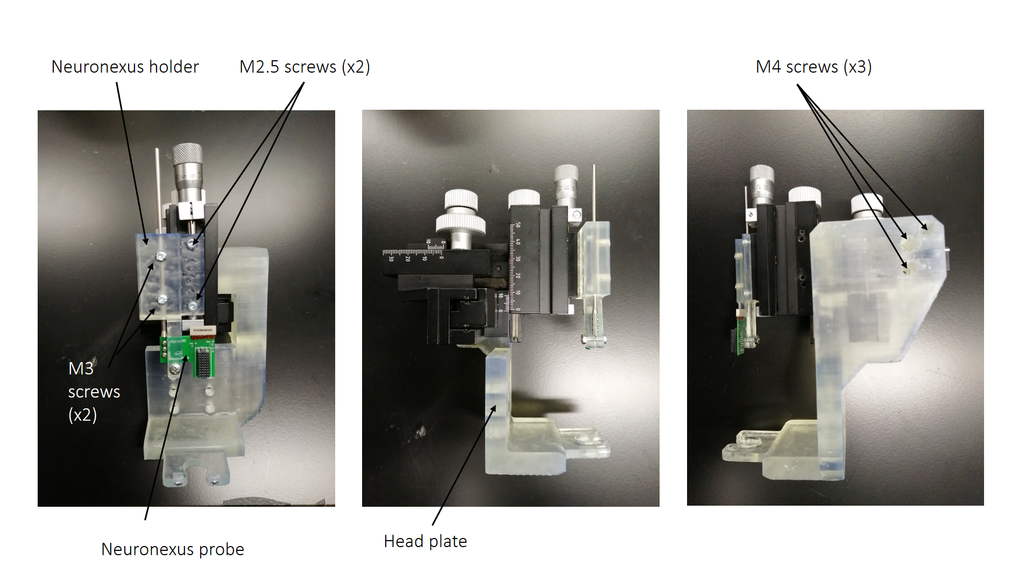
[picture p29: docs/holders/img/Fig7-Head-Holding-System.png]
|  |
| *Head-holding system assembly* |

The head-plate is secured in the head-plate holder using 2 M2.5 screws. For this end, 2 M2.5 nuts are inserted into the head-plate holder. 

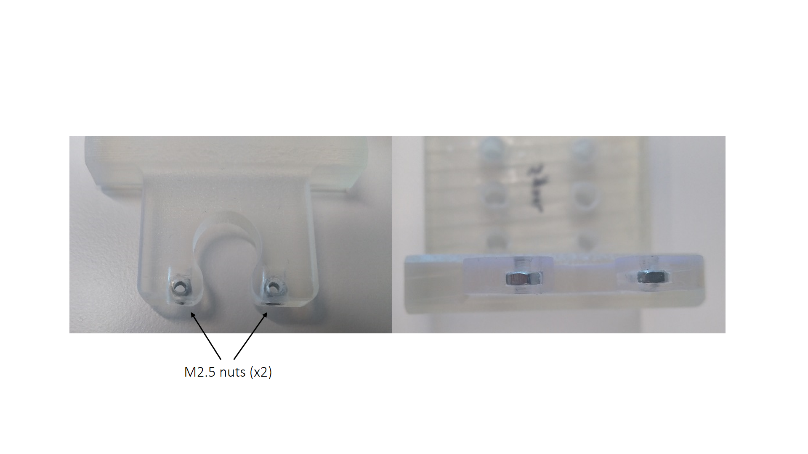
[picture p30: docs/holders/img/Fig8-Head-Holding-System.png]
|  |
|:--:|
| *Head-plate holder nuts insertion* |

Finally, the assembly is secured to the ring-shaped instrument platform with M6 screws and connected to the rotary platform using RS6P/M posts.

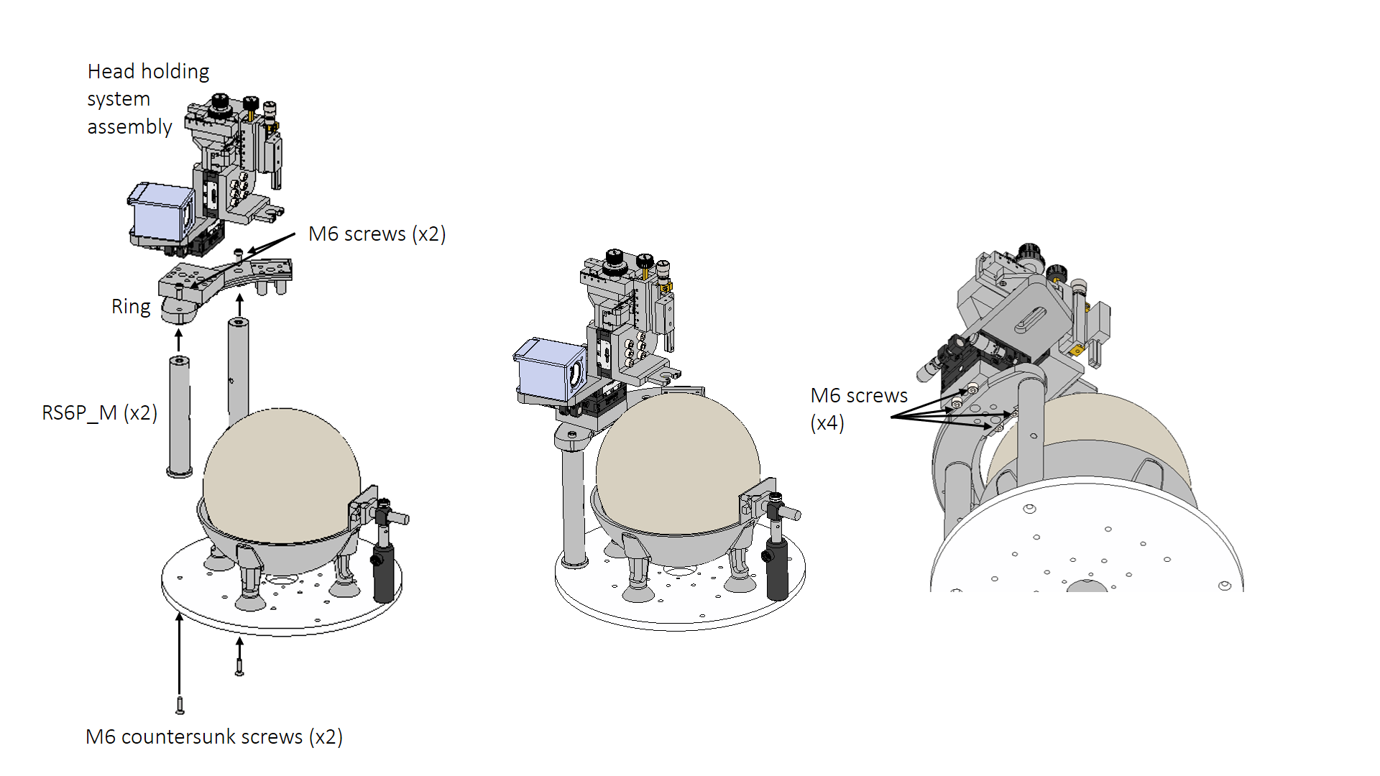
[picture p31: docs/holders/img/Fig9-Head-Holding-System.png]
|  |
|:--:|
| *Head holding system and instrument ring assembly* |

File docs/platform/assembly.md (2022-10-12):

# Assembly instructions

Start assembling the Acrylic laser cut part “Base” with the Thorlabs RS05P pedestal posts and CF175 clamping forks using M6 screws. These posts are used to attach the rotary stage to the experimental table.

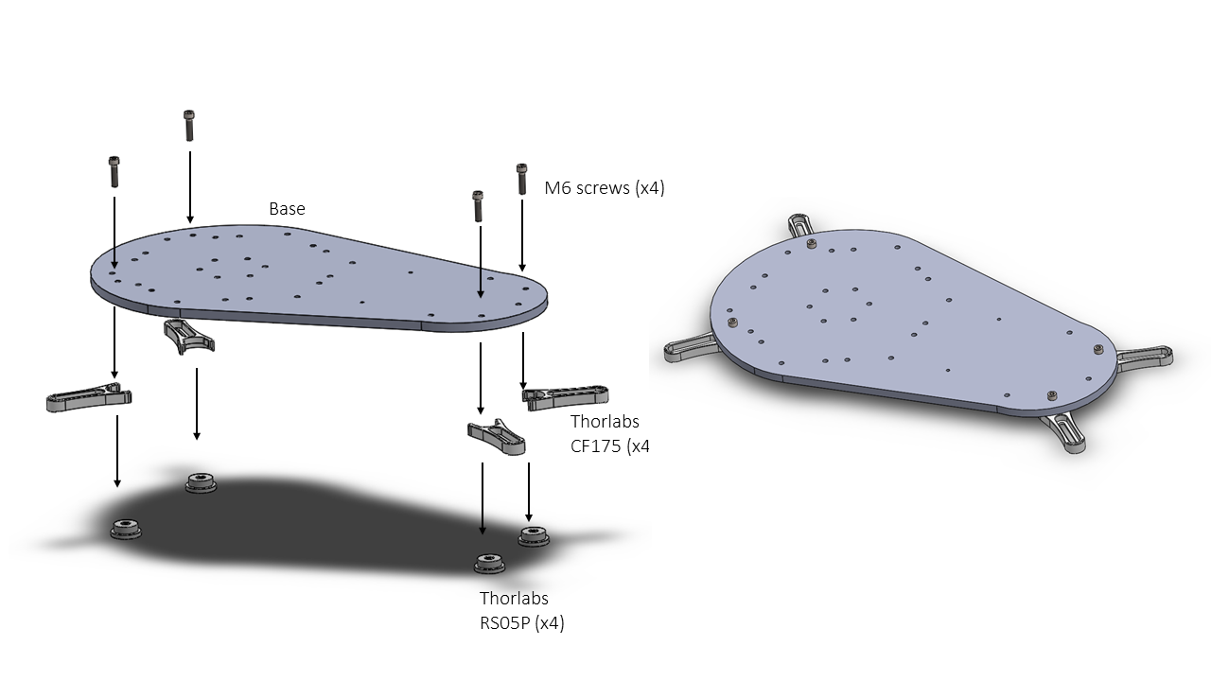
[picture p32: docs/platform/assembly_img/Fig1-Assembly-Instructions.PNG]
|  |
|:--:| 
| *Figure 1. Base assembly* |

Use two M6 screws and nuts to attach the tube guide for the compressed air tube. Attach with M6 screws the two Thorlabs posts PH_50 and the TR_50 to the base.

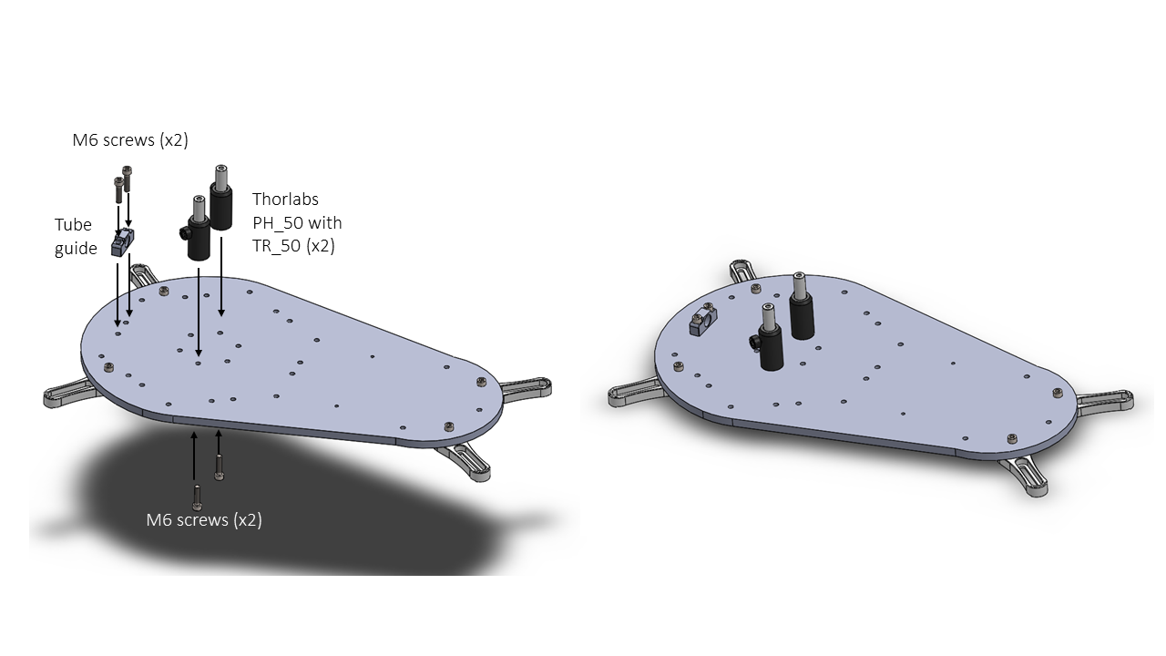
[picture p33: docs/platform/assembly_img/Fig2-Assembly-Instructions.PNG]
|  |
|:--:| 
| *Figure 2. Rotary joint telescopic posts assembly* |

The two Thorlabs PH_50 with the TR_50 are used to hold the rotary joint. To attach the rotary joint, you need two M6 or two M4 bolts with washers, depending on the position of the TR_50 (on one side is M4, on the other is M6). The compressed air tube can be installed now or at the end of the assembly.

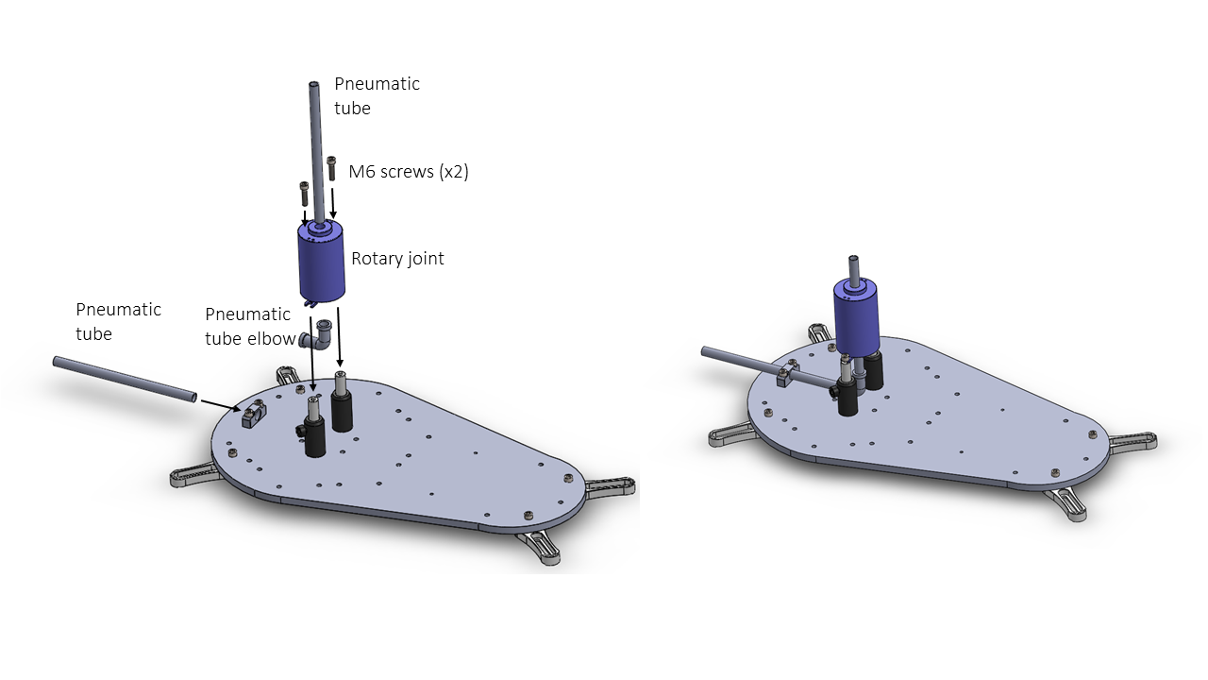
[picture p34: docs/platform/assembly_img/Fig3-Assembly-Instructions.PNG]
|  |
|:--:| 
| *Figure 3. Rotary joint assembly* |

Attach the seven Thorlabs RS150 posts to the base using M6 screws. 

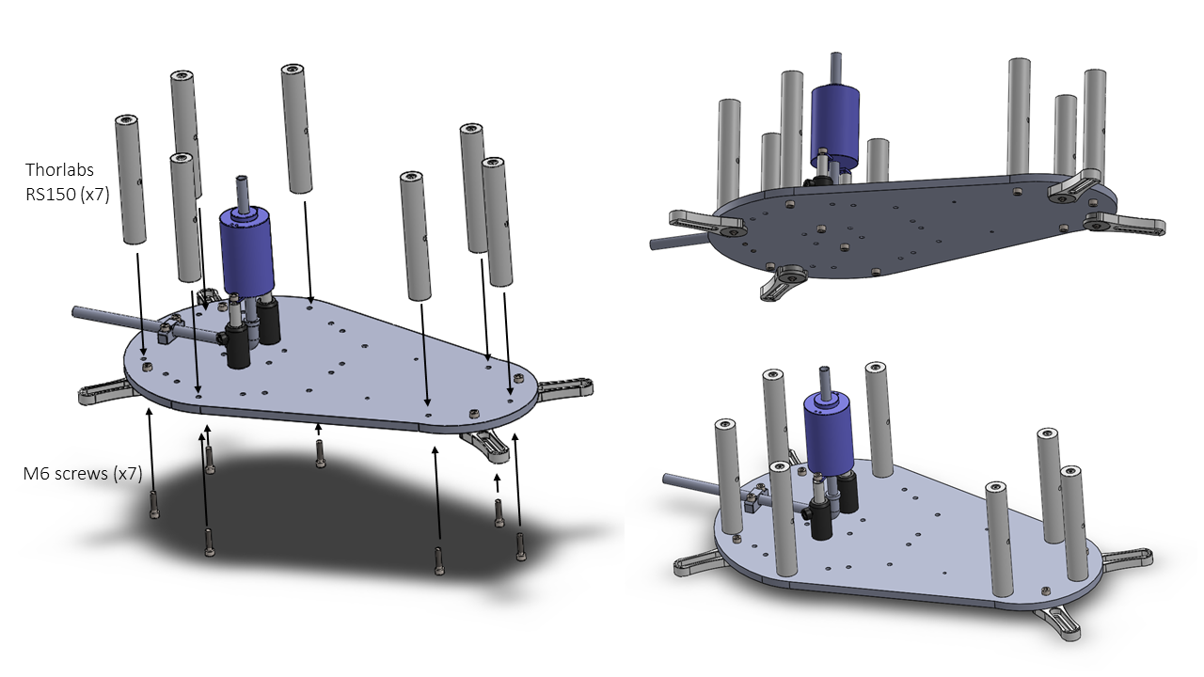
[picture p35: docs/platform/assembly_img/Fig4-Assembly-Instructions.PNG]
|  |
|:--:| 
| *Figure 4. Thorlabs RS150 assembly* |

The animation below shows the order and location of components used for the base assembly. 

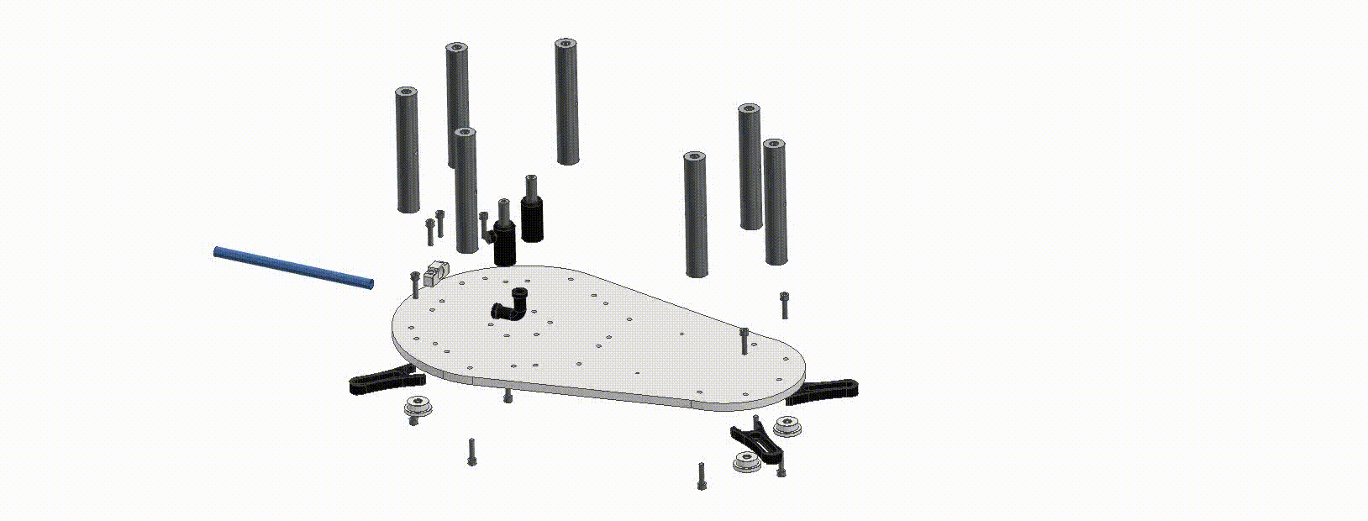
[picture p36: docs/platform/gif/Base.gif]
Gif 1
| |
|:--:| 
| *Base Assembly* |

Once the rotary joint spacer is 3D printed, insert M3 brass threaded inserts and cure the part with UV light. 

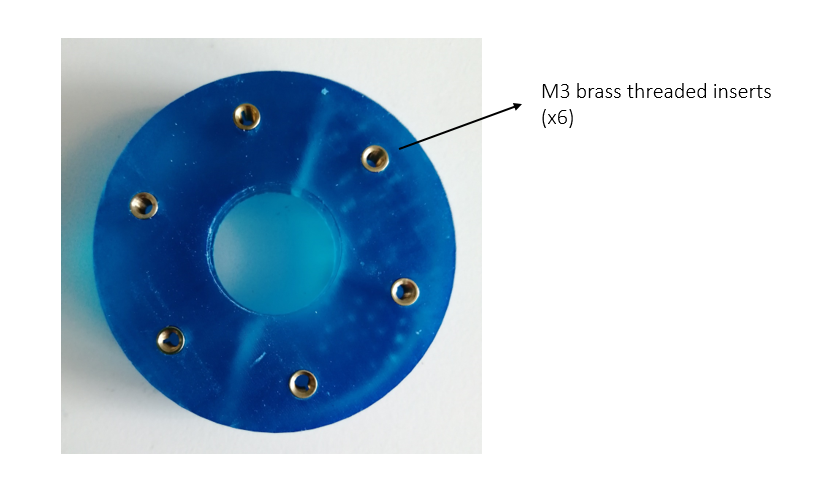
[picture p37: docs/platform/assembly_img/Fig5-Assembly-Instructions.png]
|  |
|:--:| 
| *Figure 5. Rotary joint spacer threaded inserts* |

The Rotary Joint spacer is assembled with the rotary joint using 25 mm length M3 grab-screws. These are inserted using the radial holes on the bottom of the part.

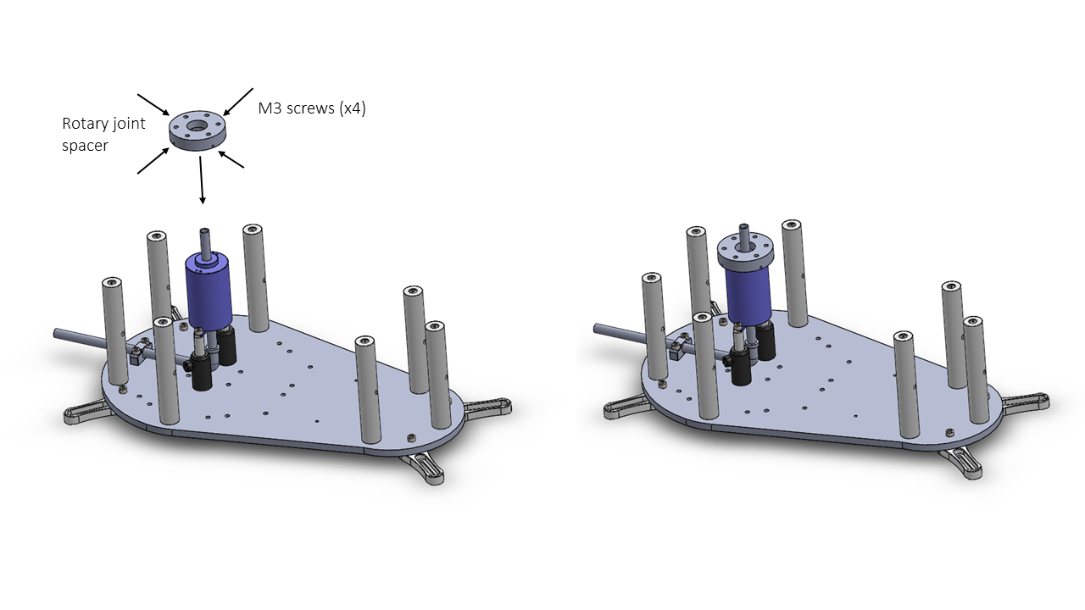
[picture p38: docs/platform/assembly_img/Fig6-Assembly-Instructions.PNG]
|  |
|:--:|
| *Figure 6. Rotary joint spacer assembly* |

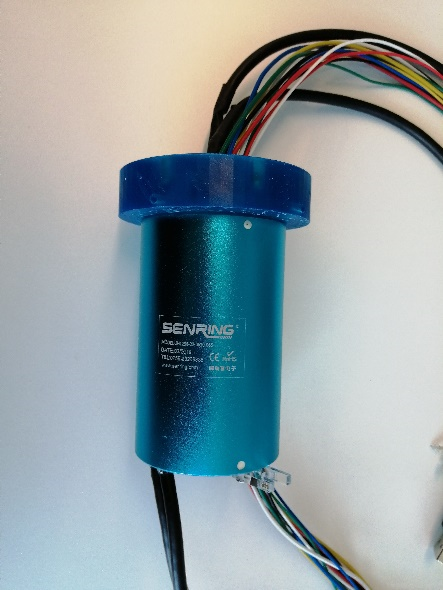
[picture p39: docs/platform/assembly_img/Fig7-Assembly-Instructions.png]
|  |
|:--:|
| *Figure 7. Rotary joint assembly* |

The crossed roller bearing BRS RU124X must be assembled with Platform 2 using ten M5 bolts and M5 nuts.

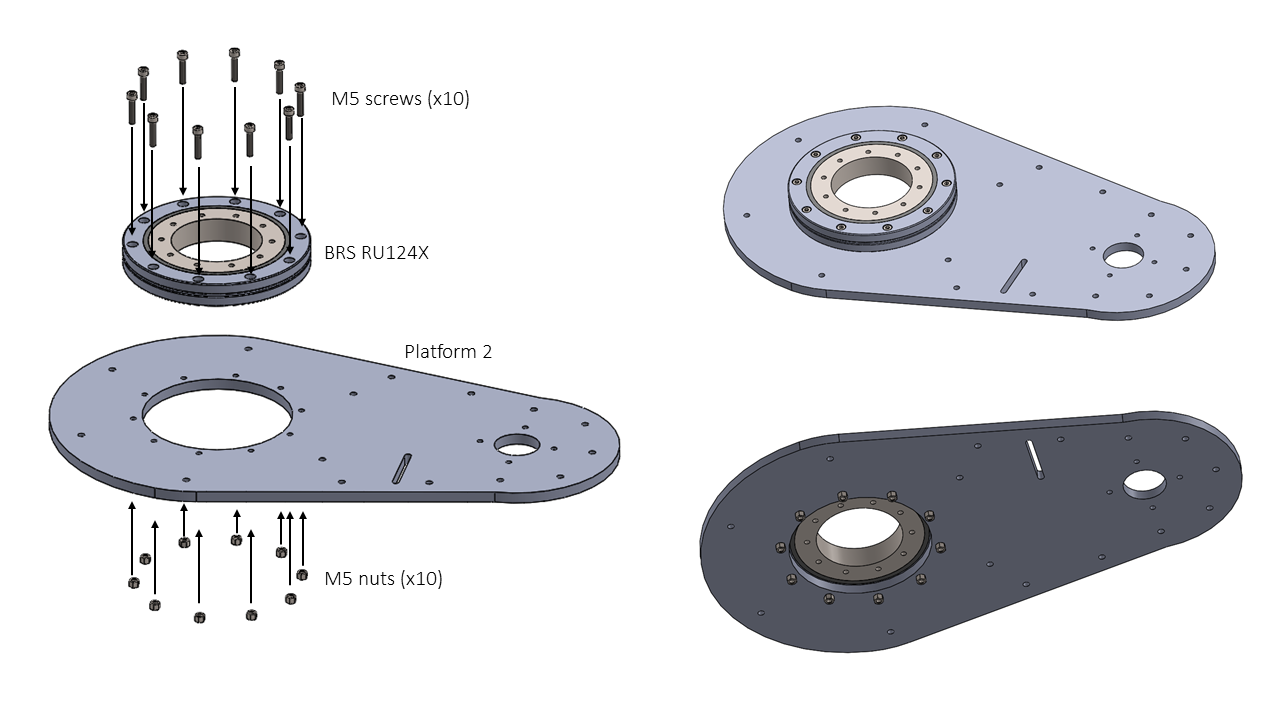
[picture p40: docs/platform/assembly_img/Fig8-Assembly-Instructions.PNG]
|  |
|:--:| 
| *Figure 8. Crossed roller bearing assembled with the Platform 2* |

The manufacturer recommends the following installation order:

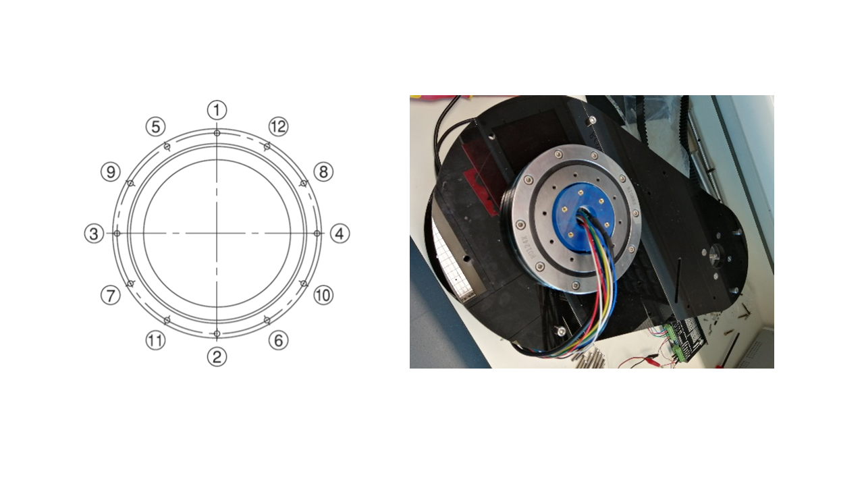
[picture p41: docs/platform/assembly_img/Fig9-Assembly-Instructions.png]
|  |
|:--:|
| *Figure 9. Crossed roller bearing installation method (left) and Cross roller bearing installed (right)* |

!!! warning
    On the laser cut part “Platform 2”, it is recommended to drill chamfers for the M4 countersunk screws that will hold the motor. This step is important because the head of the screws has to be at the same level as the surface of Platform 2. Otherwise, they might touch the pulley or the belt.

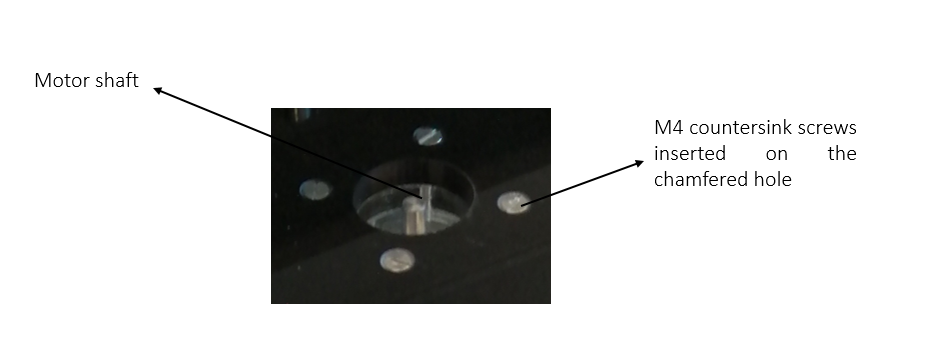
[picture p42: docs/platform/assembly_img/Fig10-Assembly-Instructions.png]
|  |
|:--:|
| *Figure 10. Detail of the countersink screws level with the surface* |

Insert the four M4 screws with their nuts to fix the Nema 23 stepper motor to the Platform 2.

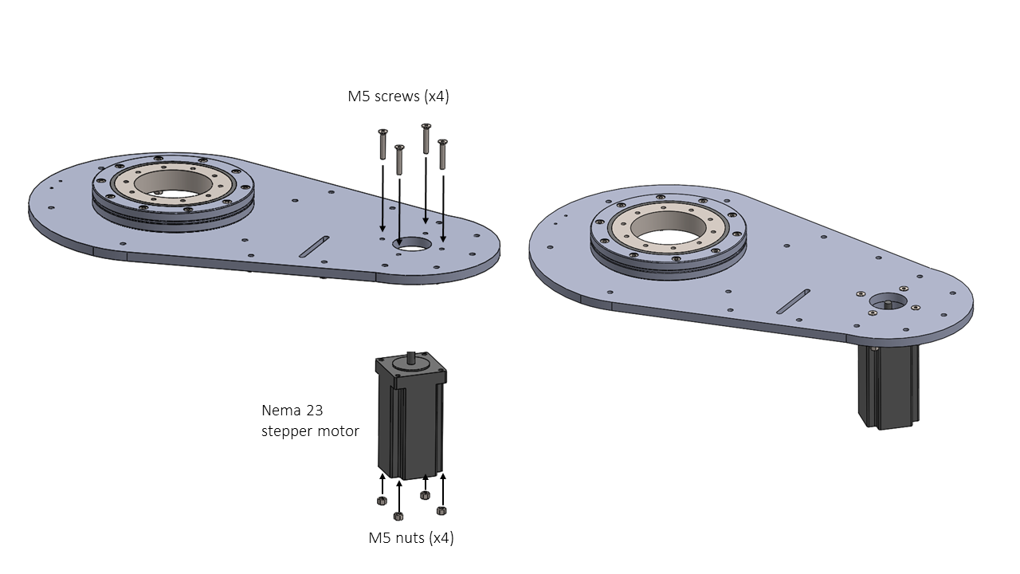
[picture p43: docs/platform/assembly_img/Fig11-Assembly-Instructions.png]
|  |
|:--:|
| *Figure 11. Motor assembly* |

The big pulley can be laser cut, as shown in Figure 12. It is composed by six layers of acrylic (2 x [layer 1](files/dxf/Big%20pulley%20(1).dxf) in 5 mm thickness, 1 x [layer 2](files/dxf/Big%20pulley%20(3).dxf) in 5 mm thickness, 2 x [layer 2](files/dxf/Big%20pulley%20(3).dxf) in 3 mm thickness and 1 x [layer 3](files/dxf/Big%20pulley%20(2).dxf) in 3 mm thickness). We recommend heating the threaded inserts with the soldering iron when inserting until they melt the plastic and go through the different layers. It is recommended to insert a couple using the external thread to get good alignment of the pulley teeth. 
Alternatively, there is an STL file to 3D print the pulley in one piece (this option has not been tested). 

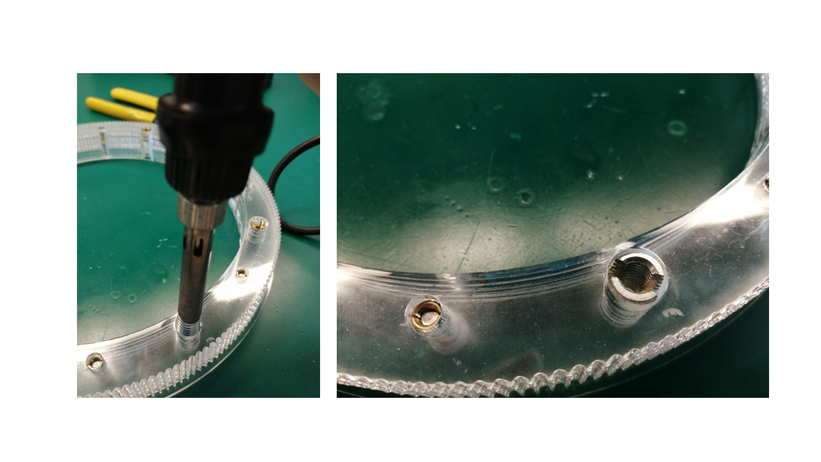
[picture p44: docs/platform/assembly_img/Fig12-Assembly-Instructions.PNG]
|  |
|:--:|
| *Figure 12. Big pulley assembly (left) and threaded inserts (right)* |

After laser cutting the circular platform, glue a small 5 mm Neodymium magnet as indicated in Figure 13. One of the magnet surfaces has to be coincident with the bottom surface of the platform. The magnet is there to interact with the Hall effect sensor at the bottom and trigger a state change to complete the homing position. Drilling chamfers on the outside holes for the countersunk screws, as seen in Figure 13, is also essential.

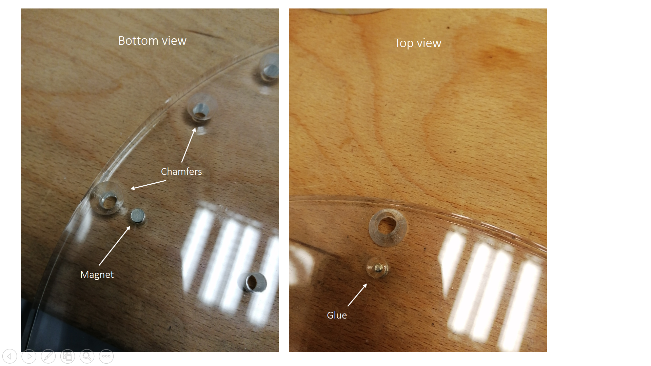
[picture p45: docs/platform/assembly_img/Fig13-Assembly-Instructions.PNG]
|  |
|:--:|
| *Figure 13. Magnet glueing and chamfers* |

Insert eight M6 screws to attach the Circular platform with the big pulley using the threaded inserts previously installed.

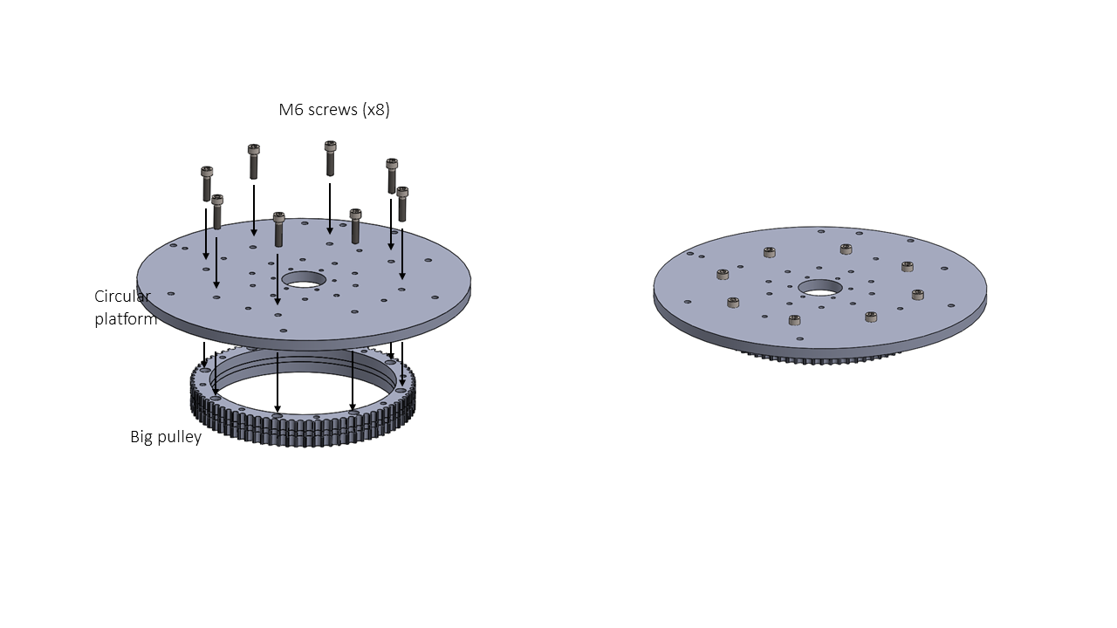
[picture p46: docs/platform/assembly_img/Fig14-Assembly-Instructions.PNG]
|  |
|:--:|
| *Figure 14. Circular platform and big pulley assembly* |

Assemble the Base with Platform 2 using 7 M6 screws.

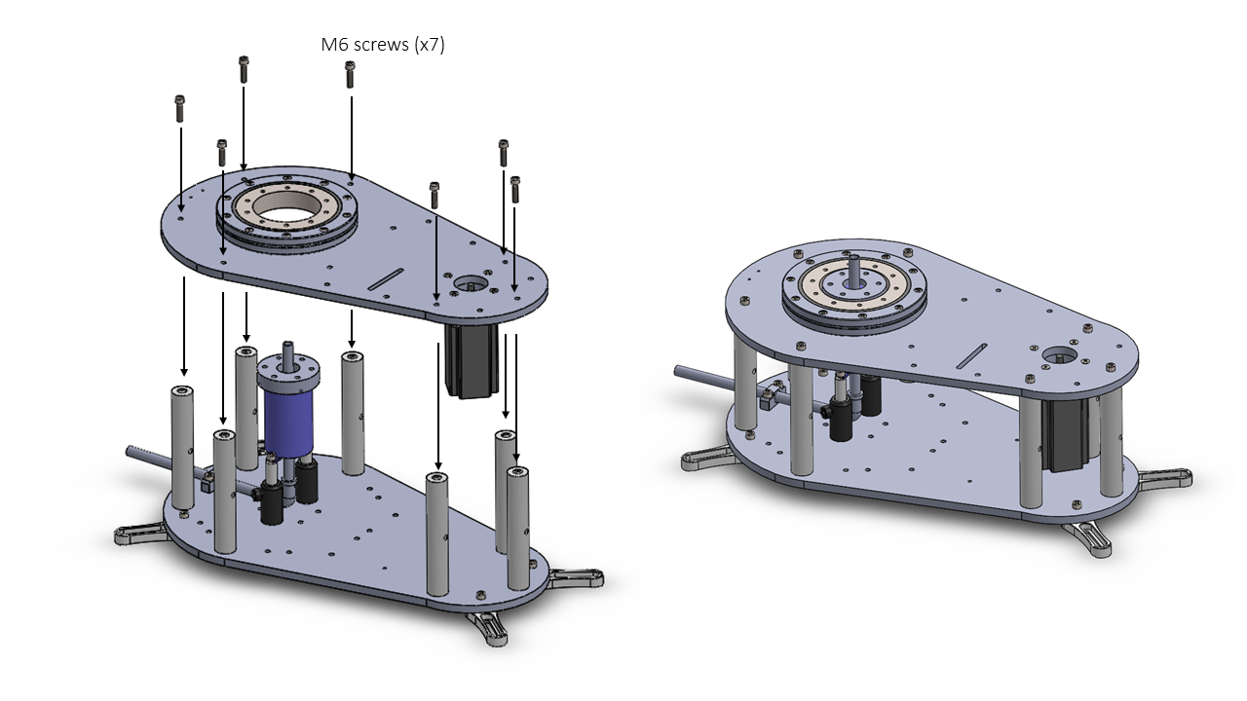
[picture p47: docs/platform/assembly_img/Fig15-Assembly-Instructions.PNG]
|  |
|:--:|
| *Figure 15. Base and Platform 2 assembly* |

The animation below shows the order and location of components used for the platform assembly. 

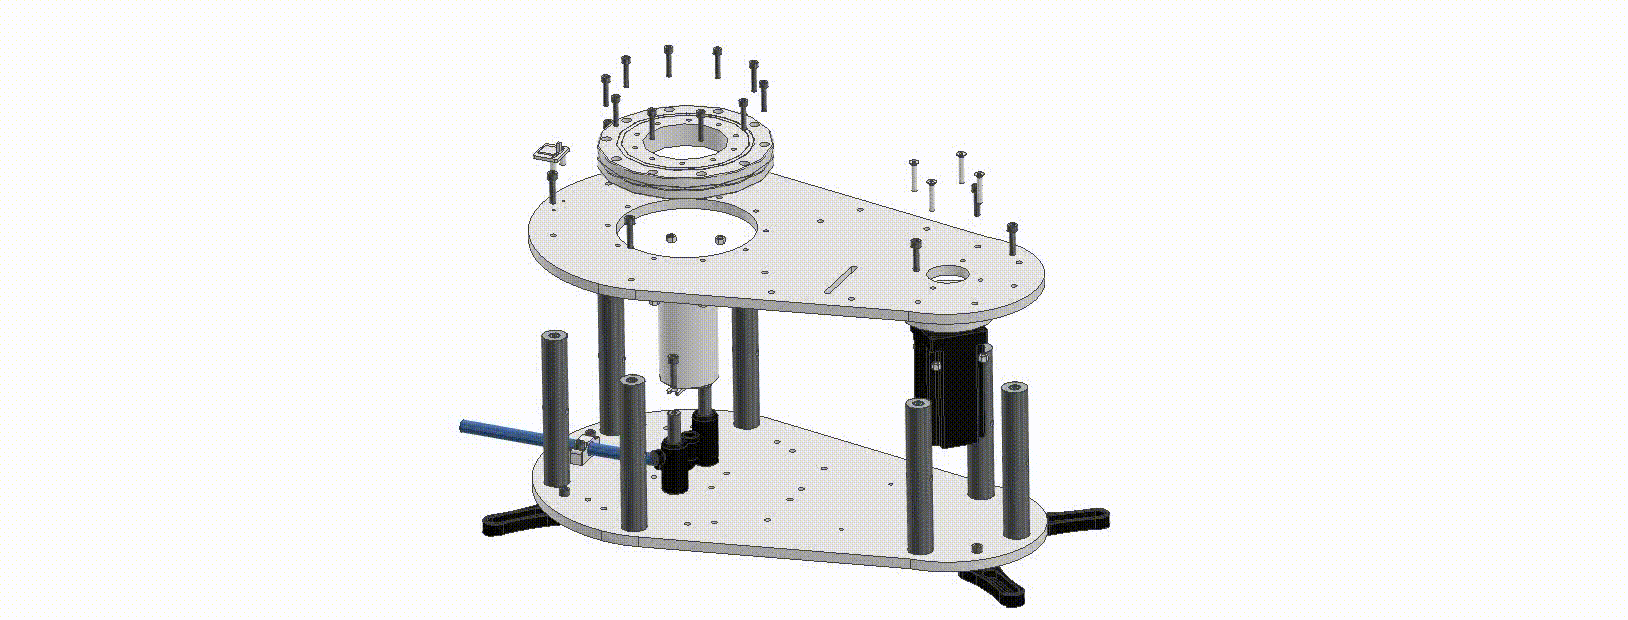
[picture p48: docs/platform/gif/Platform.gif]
Gif2
|  |
|:--:|
| *Platform assembly* |

Assemble the Hall Effect sensor used for the homing sequence, using two M3 screws, two Hall effect spacers and the Hall Effect holder.

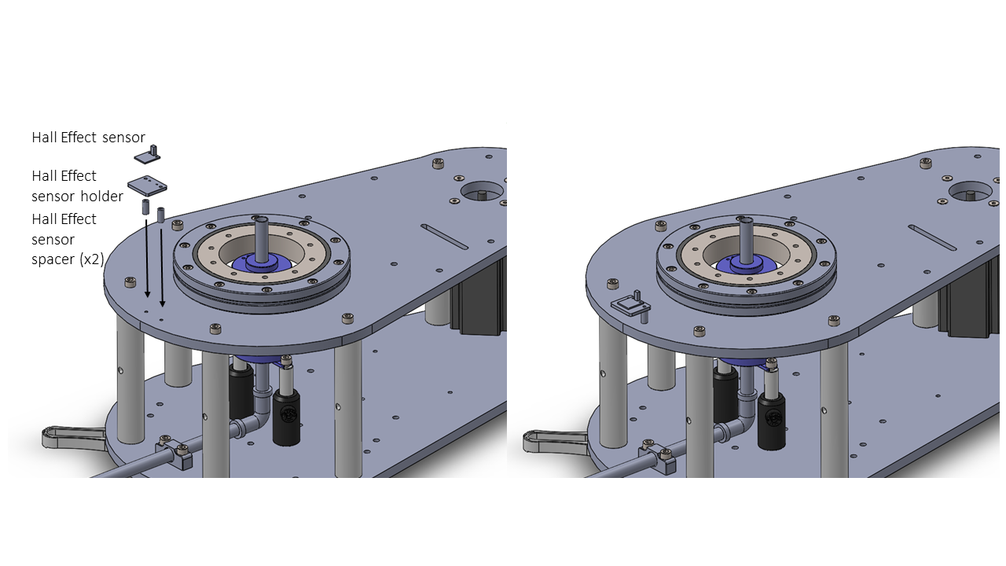
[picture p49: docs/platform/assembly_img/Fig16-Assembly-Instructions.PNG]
|  |
|:--:|
| *Figure 16. Hall Effect sensor assembly* |

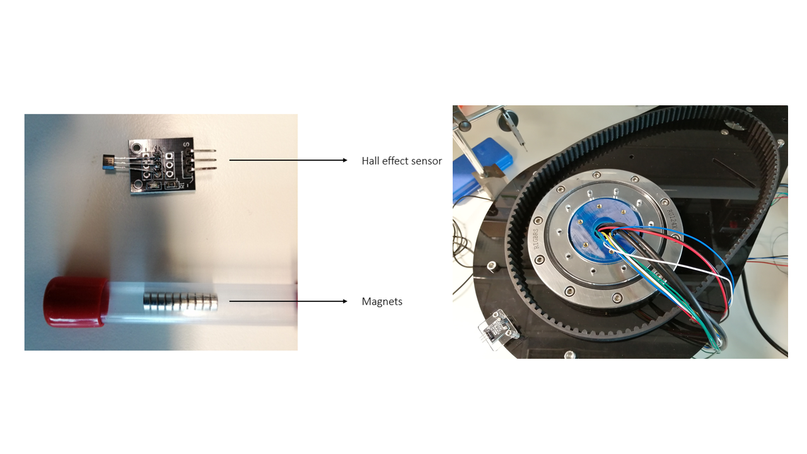
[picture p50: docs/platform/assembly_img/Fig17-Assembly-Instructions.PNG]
|  |
|:--:|
| *Figure 17. Hall effect sensor placement* |

To assemble the circular platform, place the platform spacer on the inner ring of the bearing, then place the circular platform (assembled previously with the big pulley) on the spacer and use the M5 screws also installed as in the first step of the bearing (Figure 18).

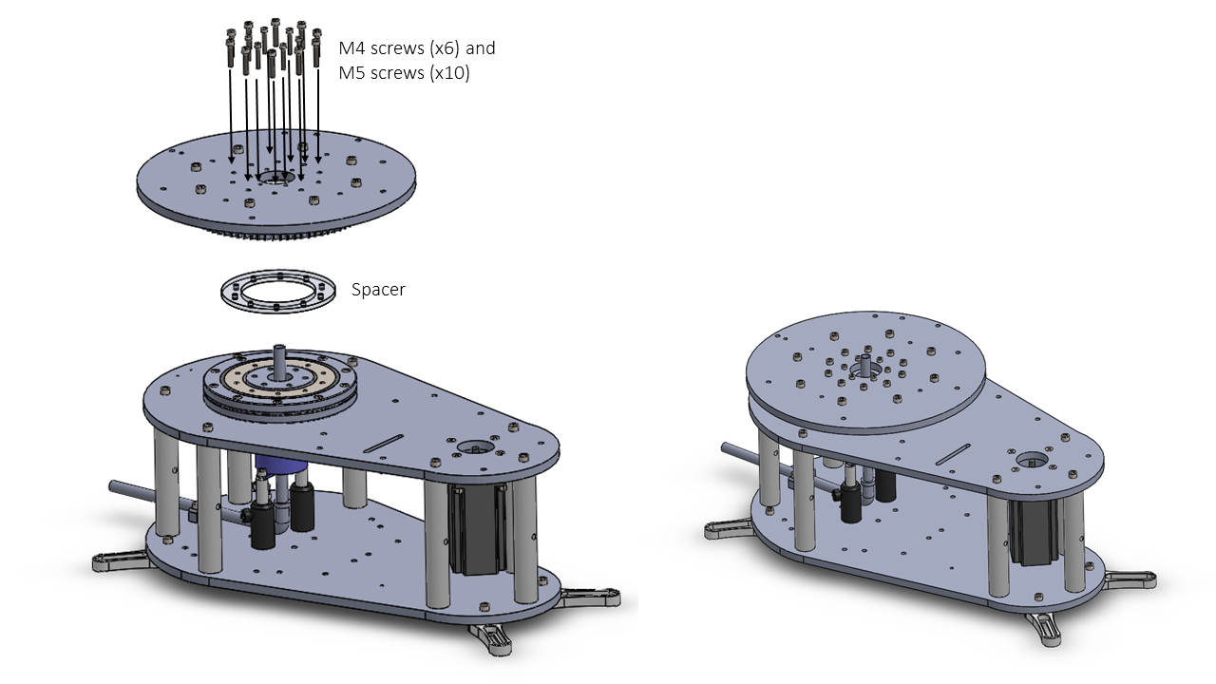
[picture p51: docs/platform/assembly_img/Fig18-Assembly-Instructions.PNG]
|  |
|:--:|
| *Figure 18. Circular platform assembly* |

The animation below shows the order and location of components used for the big pulley assembly. 

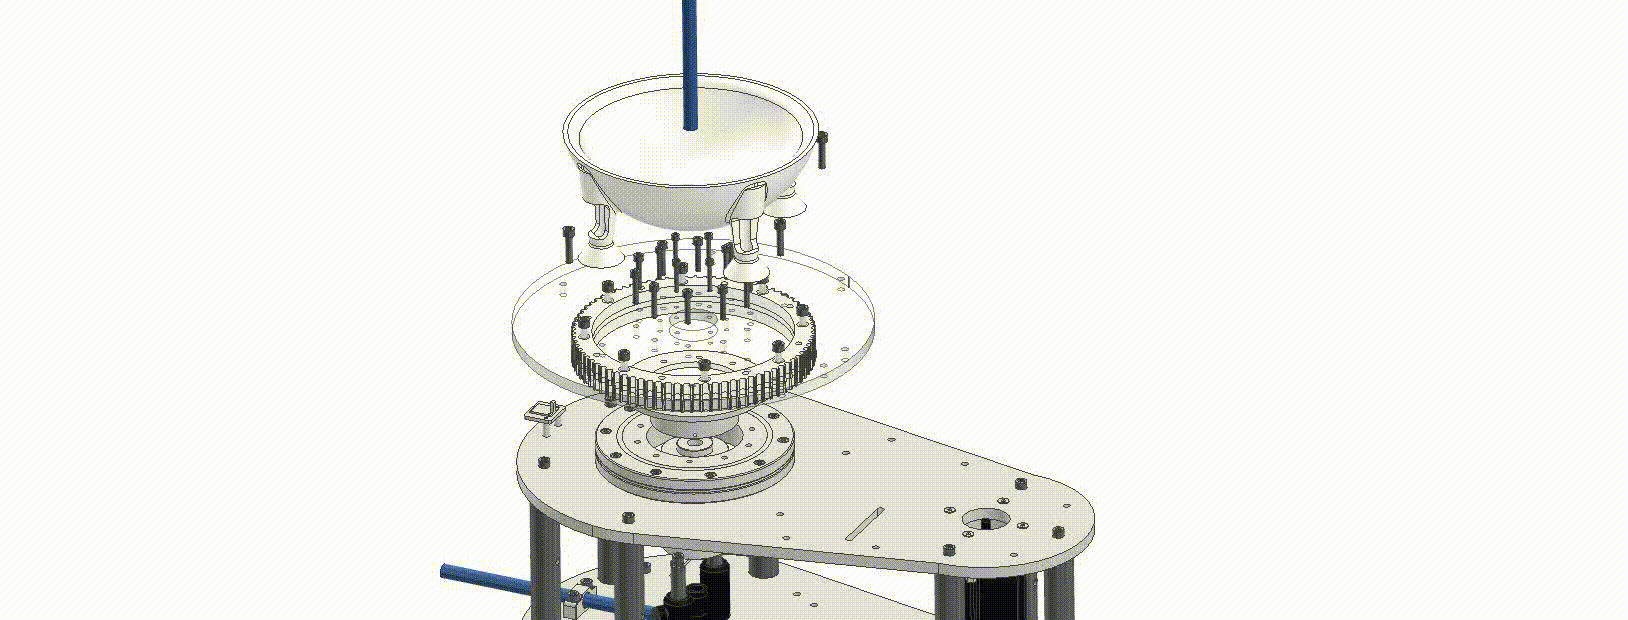
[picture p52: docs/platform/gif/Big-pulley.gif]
|  |
|:--:|
| *Big pulley assembly* |

Next, use the Thorlabs PH_50 and the TR_50 posts to adjust the height of the rotary joint spacer until it makes contact with the circular platform surface (Figure 19). Now you can insert six M4 screws to secure it.

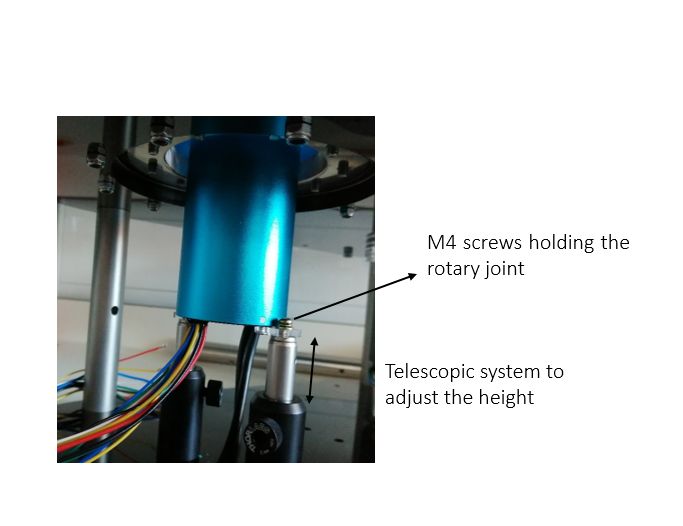
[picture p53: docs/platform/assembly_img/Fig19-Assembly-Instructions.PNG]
|  |
|:--:|
| *Figure 19. Adjustment of the Rotary joint height* |

The shaft of the Motor is 8 mm in diameter, and the inner diameter of the [small pulley](https://uk.rs-online.com/web/p/belt-pulleys/1465412/) is 6 mm. The inner diameter of the pulley has to be increased to 8 mm with a vertical drill or milling machine (Figure 20). Add a second hole with a 3.3 mm diameter (using a 3.3 mm drill bit) to add a fixing screw that prevents the pulley from rotating around the motor shaft. Thread the hole using an M4 tap toolkit. For this step, a vice is recommended to hold the pulley while drilling. To connect the encoder shaft with the pulley, the encoder attachment must be 3D printed, and two extra 2.5 mm holes must be drilled at the top of the pulley. Then, an M3 thread must be made using the M3 tap tool. 

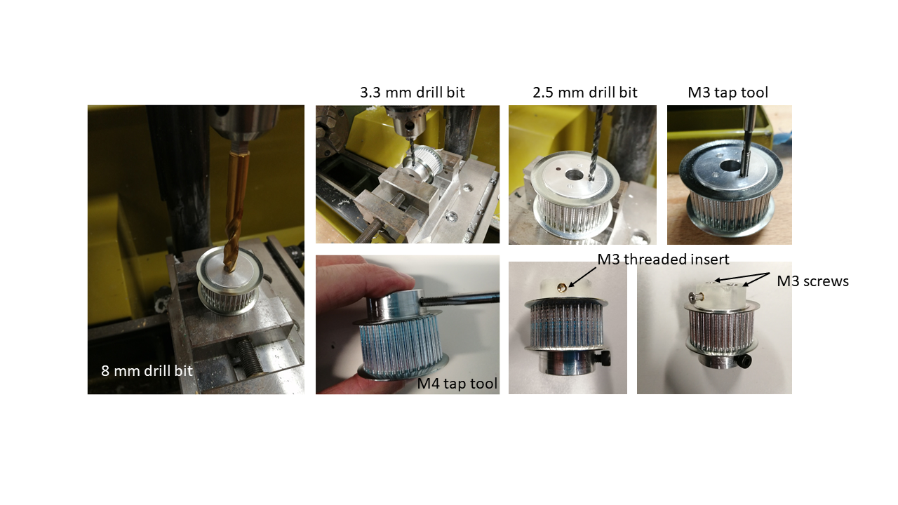
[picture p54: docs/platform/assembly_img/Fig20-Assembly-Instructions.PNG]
|  |
|:--:|
| *Figure 20. Small pulley* |

The pulley can be assembled before or after attaching the motor to platform 2.

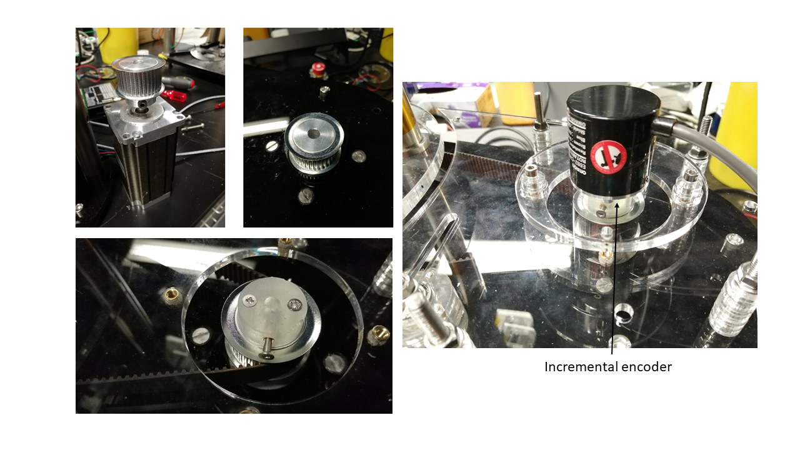
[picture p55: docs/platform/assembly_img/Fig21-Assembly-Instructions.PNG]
|  |
|:--:|
| *Figure 21. Small pulley and encoder* |

The belt must envelop the small pulley when you put it on the motor shaft. You will feel a high tension when pulling the belt since it is rigid. 

!!! warning
    Remember to put the flat part of the motor shaft oriented in a comfortable position to secure with the small pulley M4 screw afterwards.

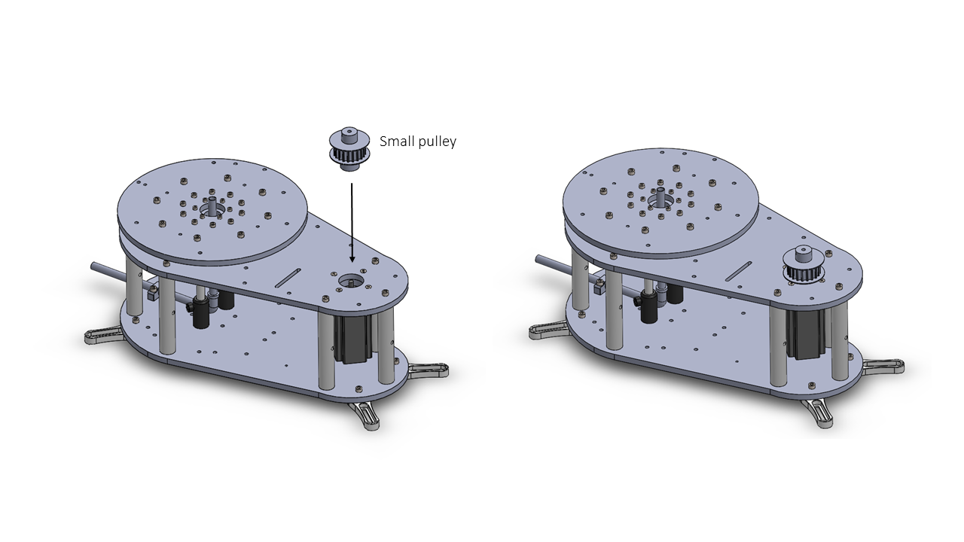
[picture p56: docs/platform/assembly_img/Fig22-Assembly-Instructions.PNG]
|  |
|:--:|
| *Figure 22. Small pulley with motor shaft assembly* |

Three M3 screws are used to attach the Encoder holder to the encoder.

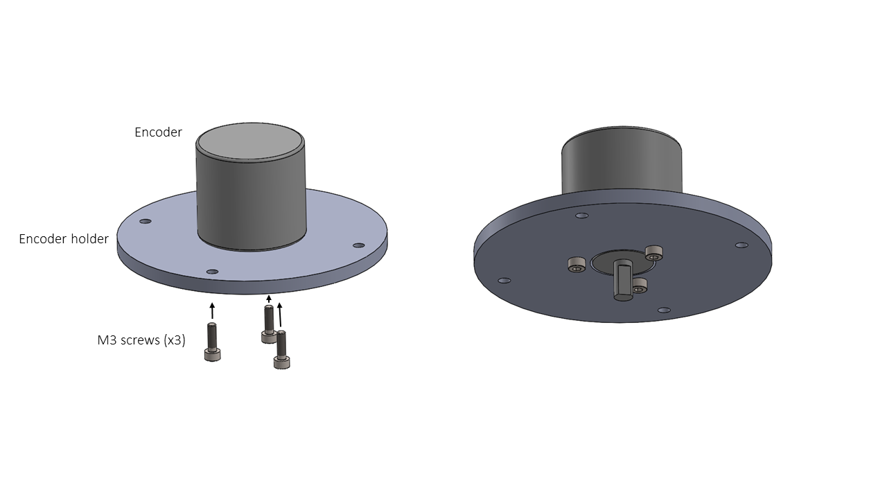
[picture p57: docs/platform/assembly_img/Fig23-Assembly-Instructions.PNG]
|  |
|:--:|
| *Figure 23. Encoder holder and encoder assembly* |

Once the belt cover part is laser cut, four brass M4 threaded inserts must be inserted into the holes by heating them with the soldering iron or applying pressure.

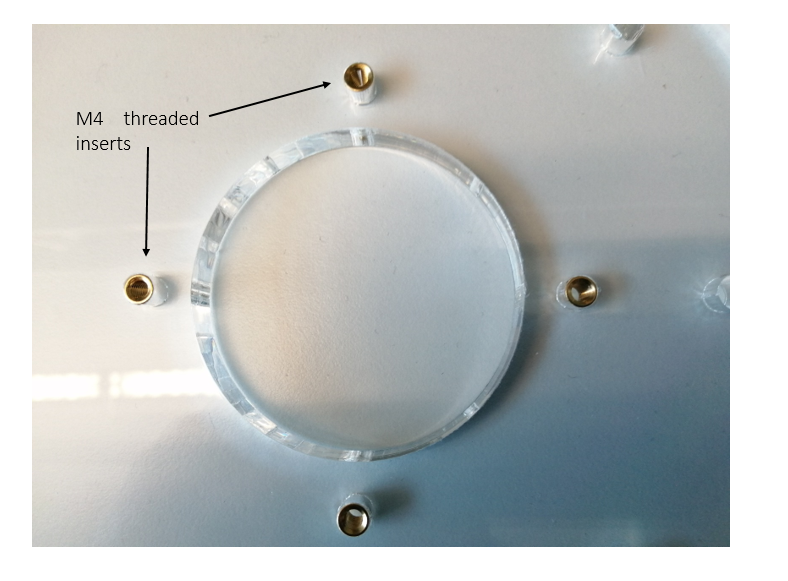
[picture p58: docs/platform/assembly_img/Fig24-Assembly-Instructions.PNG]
|  |
|:--:|
| *Figure 24. M4 threaded inserts on the belt cover* |

Now four M4 screws can be inserted from the top placing the encoder spacers coincident with the holes.

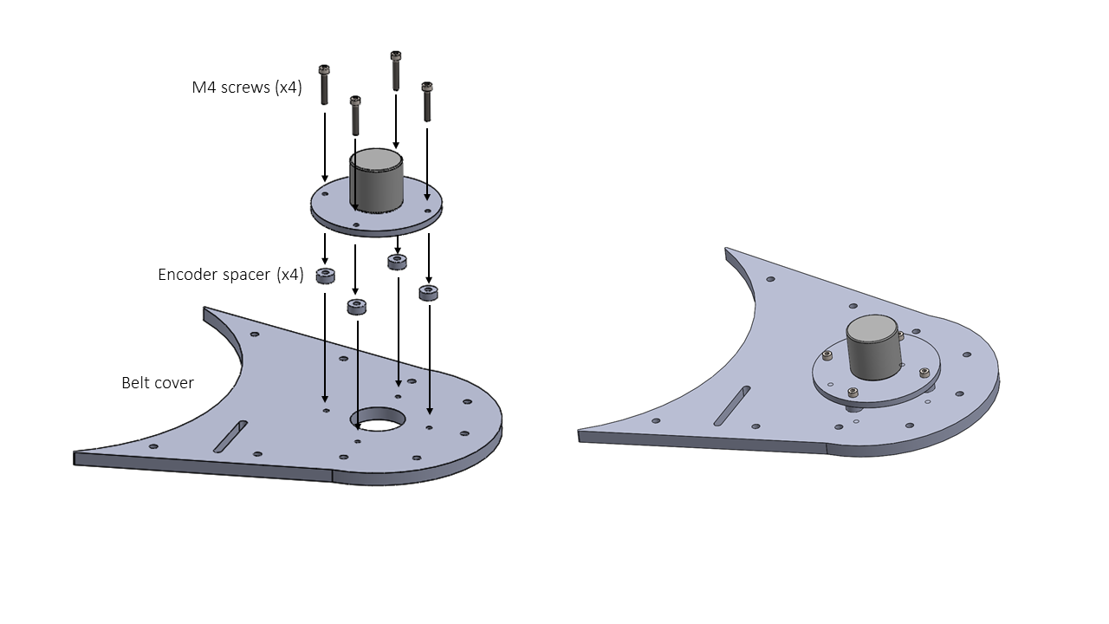
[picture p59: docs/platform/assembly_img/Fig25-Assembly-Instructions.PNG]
|  |
|:--:|
| *Figure 25. M4 threaded inserts on the belt cover* |

The belt cover can now be installed using M6 screws, nuts and the cover spacers. After that, the encoder shaft must be in contact with the M4 grub screw at the top of the pulley.

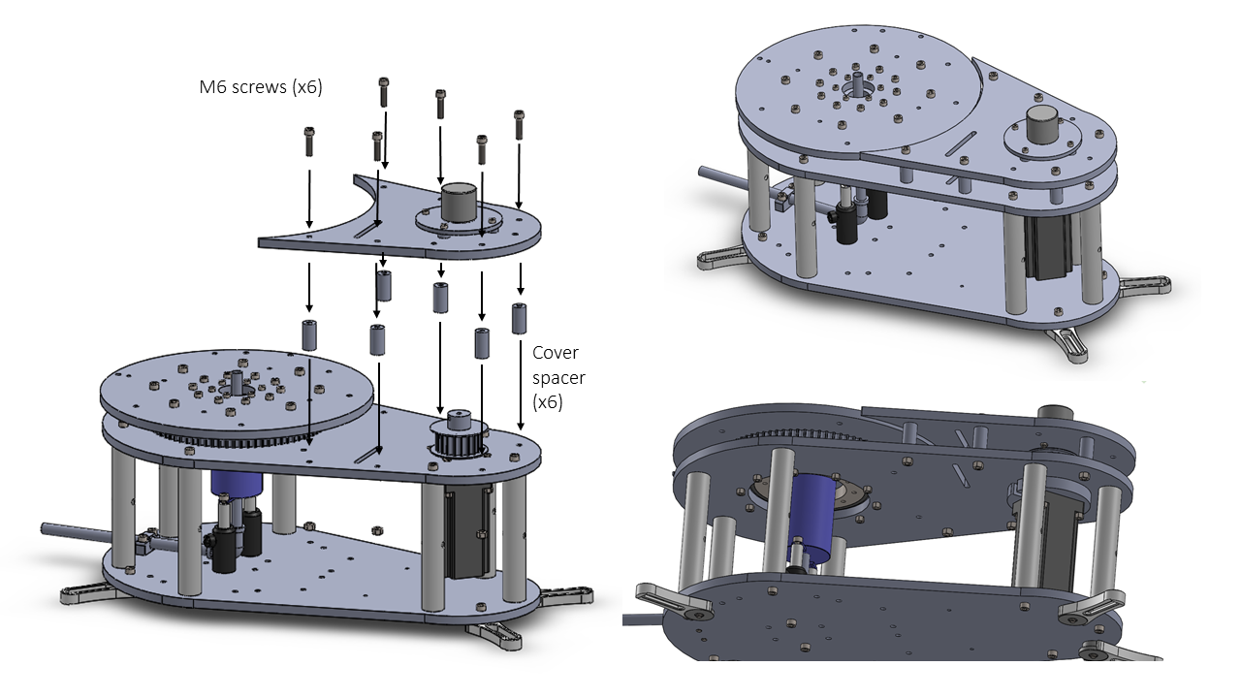
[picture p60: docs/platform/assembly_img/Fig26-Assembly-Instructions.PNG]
|  |
|:--:|
| *Figure 26. Belt cover assembly* |

The animation below shows the order and location of components used for the small pulley assembly. 

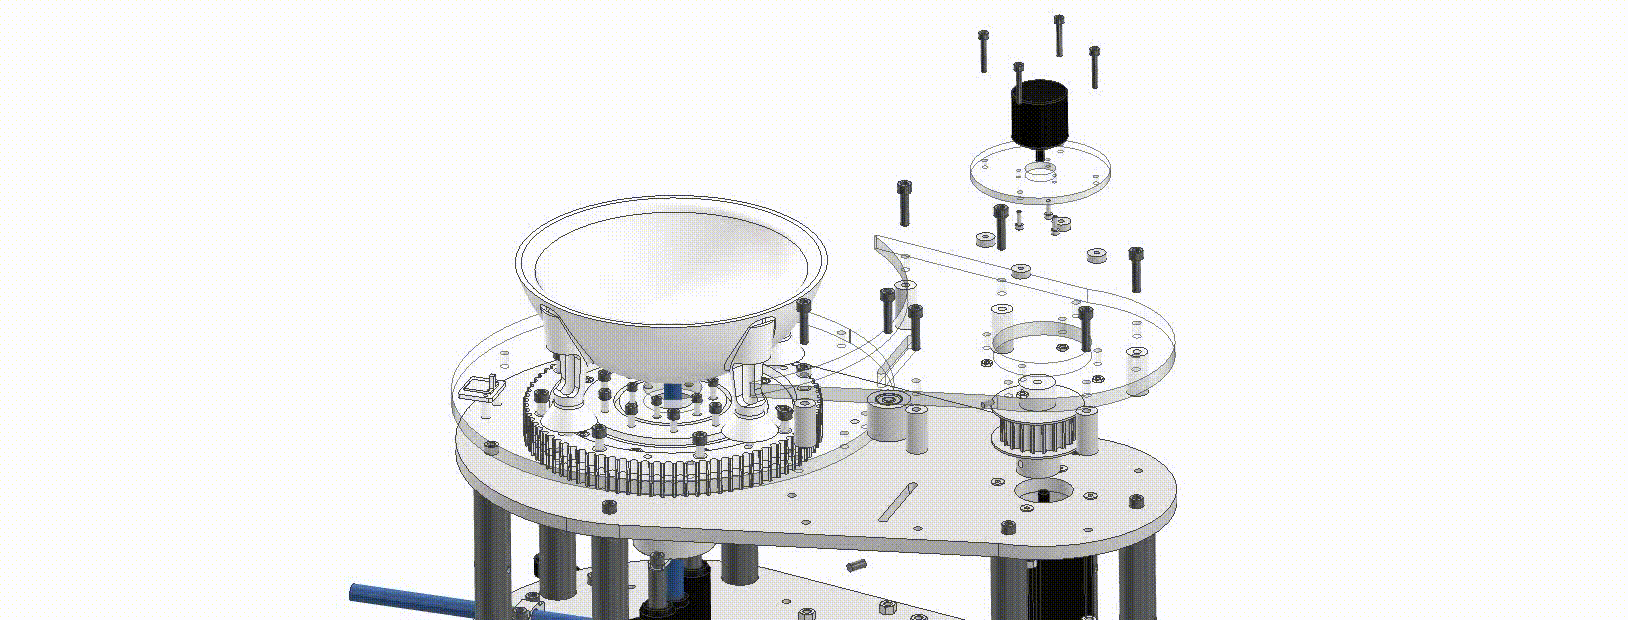
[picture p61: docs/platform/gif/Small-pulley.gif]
|  |
|:--:|
| *Small pulley assembly* |

To regulate the belt's tension, two ball bearings are inserted on the belt tensor, and one M6 screw is used to install it in the guide. Use four washers to get a good fit on the inside and outside of the screw with the two sides of the belt cover and Platform 2.

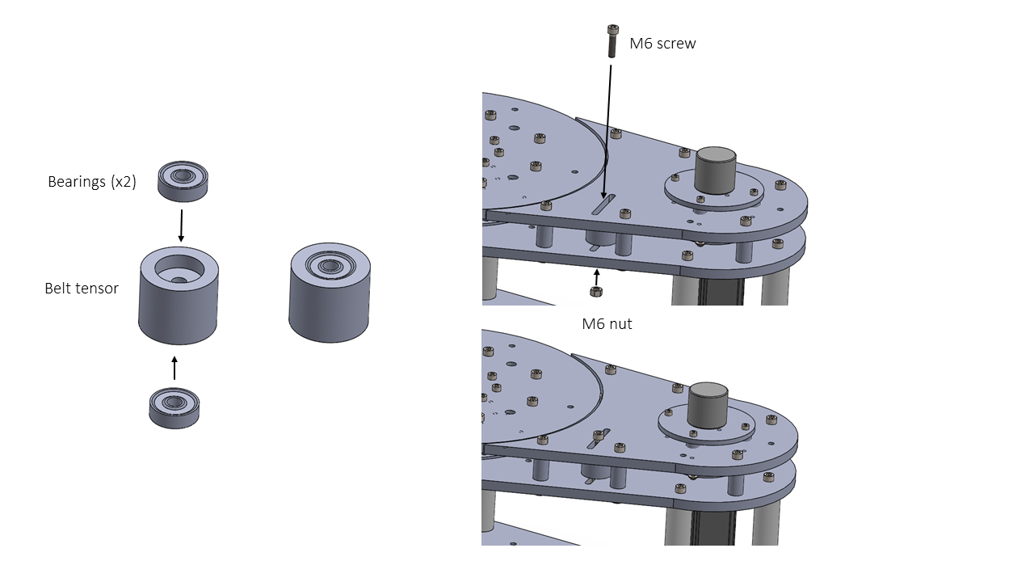
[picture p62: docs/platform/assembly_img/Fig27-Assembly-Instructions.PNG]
|  |
|:--:|
| *Figure 27. Belt tensor assembly* |

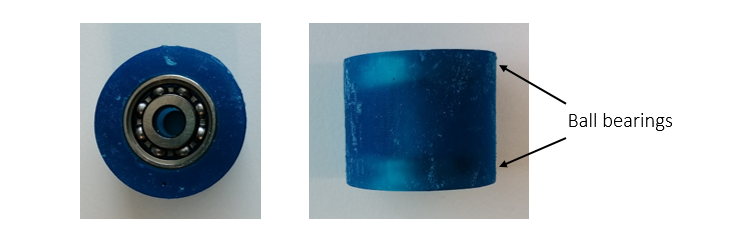
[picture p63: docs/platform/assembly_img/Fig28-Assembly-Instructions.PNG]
|  |
|:--:|
| *Figure 28. Detail of the two ball bearings* |

Now adjust the tension of the belt. Check the belt is not touching the bottom or the top surfaces.

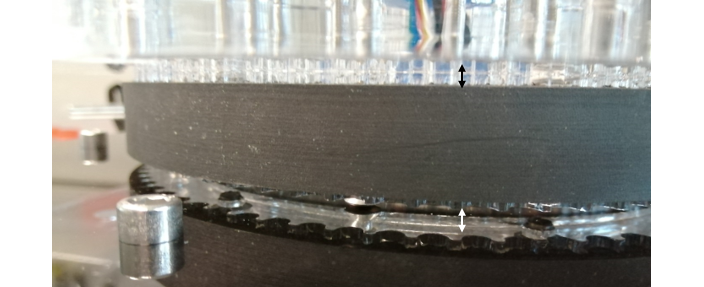
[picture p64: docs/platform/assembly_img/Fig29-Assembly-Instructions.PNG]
|  |
|:--:|
| *Figure 29. Space on both sides of the belt* |

The vertical tubing for compressed air can now be inserted through the rotary joint through-hole into the pneumatic tube elbow. Lastly, the sphere holder has to be attached with four M6 screws.

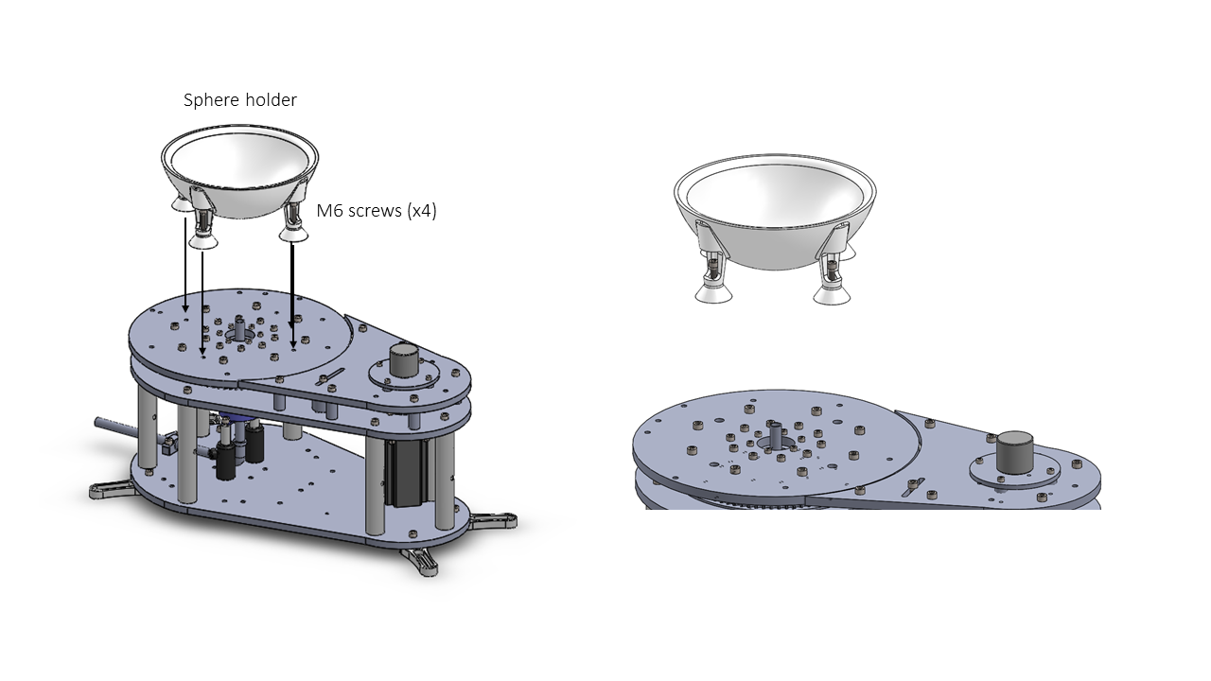
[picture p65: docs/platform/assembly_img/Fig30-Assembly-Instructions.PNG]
|  |
|:--:|
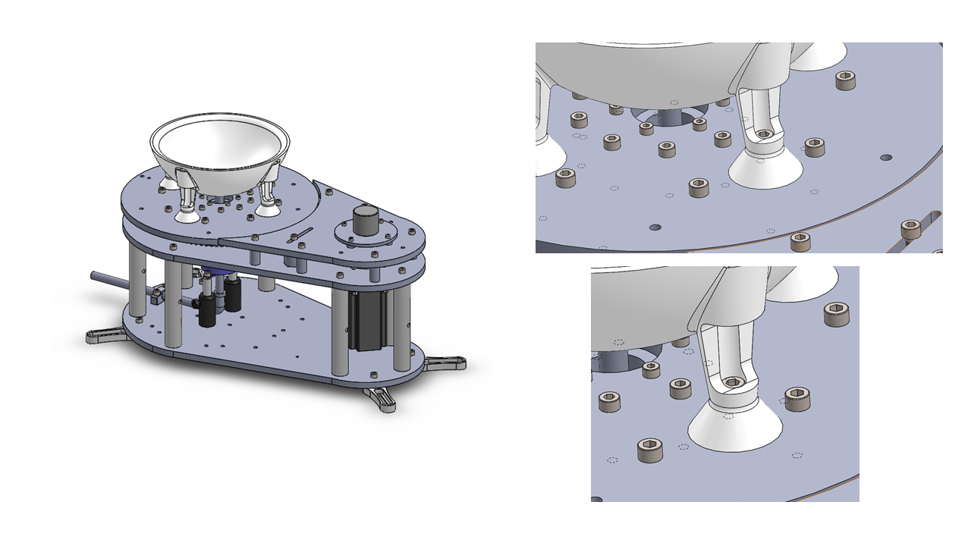
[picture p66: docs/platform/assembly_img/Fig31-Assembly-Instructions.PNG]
|  |
| *Figure 30-31. Sphere holder assembly* |

|  |
|:--:|
| *Figure 32. Complete assembly* |

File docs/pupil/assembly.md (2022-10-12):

# Assembly instructions

-	Cut 2 pieces of silicone tube to similar lengths as the mirror edges (36 mm and 25 mm).
-	Glue both parts into the mirror holder.
-	Use a scalpel to make a longitudinal cut along both tubes.
-	Insert a 6 mm diameter Thorlabs post into the mirror holder.

|  |
|:--:|
| *Figure 1. Mirror holder assembly* | 

-	Use a 3D printing material with opaque features (e.g. FormLabs black resin). If using clear resin, use black matt spray to block out external light. 
-	Use 4 M2 screws and nuts to attach the camera to the camera holder.
-	Insert the filter, mounted on a CP35/M and an SM1L03 lens tube in the filter holder. Use 4 M3 screws to attach it to the filter holder cover.
-	Use two long (25-30 mm) M3 screws as shafts to open and close the filter holder.	

|  |
|:--:|
| *Figure 2. Camera and filter holder assembly* | 

-	Use an M6 screw and nut to attach the camera holder to the MT1/M linker with the camera holder lip found in the "Instrument ring and head holder" section.

|  |
|:--:|
| *Figure 3. Camera assembly to head-fixation system* | 

-	Attach the mirror holder to the instrument ring or the rotation platform using Thorlabs components (e.g. RA90TR/M and 12.7 mm post).
-	Mount the head fixation system onto the instrument ring.

|  |
|:--:|
| *Figure 4. Camera and mirror* |

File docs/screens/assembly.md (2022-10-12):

# Assembly instructions

To assemble the screen, the display and the front and back screen holders need to be attached using spacers, M4 screws and nuts.

|  |
|:--:|
| Gif1 |
| *Figure 1. Screen assembly* |

Separately assemble the 3D printed Screen attachment 1 with the back of the Screen holder.

|  |
|:--:|
| *Figure 2. Front holder assembly* |

Attach the electronic board with the screen holder back using 3 M3 screws and nuts. Then attach the two back holders with M4 screws.

|  |
|:--:|
| *Figure 3. Back holder assembly* |

|  |
|:--:|
| *Figure 4. Location of the screens on the platform* |

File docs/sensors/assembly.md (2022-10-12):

# Assembly instructions

The PCB must be removed from the optical mouse first. Then the VDD, GND, SCK and SDIO pins must be soldered to wires leading to the microcontroller and its internal 5V power supply.

|  |
|:--:|
| *Figure 1. Soldered pins on the ADNS-2610* |

Insert the two M3 brass threaded inserts into the sensor holder by applying pressure. 
Attach the sensor to the sensor holder using 2 M3 screws.

|  |
|:--:|
| *Figure 2 Optical sensor assembly* |

Then follow the instructions in Figure 3 to assemble the three Thorlabs components with the sensor holder.

|  |
|:--:|
| *Figure 3. Optical sensor assembly* |

The lens must be glued to the PCB in the correct position, with the lens aligned with the optical flow sensor.

|  |
|:--:|
| *Figure 4. ADNS-2610 glued with the lens* |

Attach the whole assembly on the rotary stage platform (e.g. at 0 or 90 degrees to the animal's anteroposterior axis).

|  |
|:--:|
| *Figure 5. Optical sensor – platform assembly* |

Connect the pins on the PCB 5V, GND, and two digital pins as shown on the "electrical setup and configuration" page.

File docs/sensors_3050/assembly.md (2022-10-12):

# Assembly instructions

The PCB and the lens must be removed from the optical mouse. The VDD, GND, MISO, MOSI, NCS and SCLK must be soldered to wires leading to the microcontroller with the microcontroller 3.3V power supply output. The SCLK is the clock selected on the ADNS-3050.h C++ library (in our case 4 MHz, the internal clock divided by 21 of the Arduino DUE used for the SQUAL measurements). The NCS pin allows communication with more than one device by changing the state to HIGH or LOW. The MOSI and MISO pins are to send the data in both directions.

|  |
|:--:|
| *Figure 1. Soldered pins on the ADNS-3050* |

The lens and the PCB are assembled with the PCB holder part 1 and 2 by placing the lens as in Figure 1 and inserting the screws to attach both parts together. 

|  |
|:--:|
| *Figure 2. ADNS-3050 and lens assembled with the PCB holder.* |

The provided library was created by Tom Wiggins and is available on GitHub [[1]](#references) and Hackaday [[2]](#references). The library has been modified duplicating the functions needed to control and get data from two optical mice.

# References

[1] [https://github.com/Tom101222/Adns-3050-Optical-Sensor](https://github.com/Tom101222/Adns-3050-Optical-Sensor)

[2] [https://hackaday.io/project/18344-adns-3050-optical-sensor-mouse](https://hackaday.io/project/18344-adns-3050-optical-sensor-mouse)

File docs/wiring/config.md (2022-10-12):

# Motor driver configuration

The configuration of the stepper motor driver shown below for the position control corresponds to 25,000 steps per revolution on the motor shaft (150,000 steps per revolution on the rotary table):



NOTE. To control the closed loop response, we have explored how the different configurations of micro-stepping of the driver DM542A match with the internal units of the optical motion sensor. In the case of the ADNS 2610, the measured average number of internal units per revolution is 9,391 and therefore the best micro stepping configuration is 25,000 steps per revolution.
We have evaluated the relationship between the number of steps and the sensor internal units in each possible micro-stepping configuration. The number of steps on the big pulley is 150,000 steps with a gear ratio of 6 between the small and big pulley. Therefore, the number of steps per optical sensor unit is 15.97 steps. This configuration is also the most silent and helps reduce vibrations on the platform. 

We have used the TeensyStep library [[1]](#references) which can control stepper motors precisely at high speeds (300,000 steps/s) and accelerations (500,000 steps/s^2). We have implemented a proportional control between the angle measured on the Styrofoam sphere as a set point and the angle of the stepper motor measured from the internal counter of the stepper object using the method stepper.getPosition() [[2]](#references). The proportional control uses the method controller.overrideSpeed() to change the rotational speed on the fly.

equation1

The encoder can be used to record the position separately or implement closed-loop control using the encoder as a position reference.

The range of speed and acceleration we have tested with the rotary stage vary from 20 to 100 deg/s and 200 to 1200 deg/s^2.

The main loop() execution period on the Teensy 3.5 at 120 MHz is approximately 270 µs therefore the program execution frequency is higher than 3 kHz where the position of the sensor is evaluated and sent to the stepper motor.

!!! warning
    If the speed is increased, the system will tend to overshoot. The proportional constant (kp) of the control algorithm might have to be adjusted to get better performance. Using the kp in our code examples, we always got good results.

# References

[1] [https://luni64.github.io/TeensyStep/](https://luni64.github.io/TeensyStep/)

[2] [https://forum.pjrc.com/threads/43491-New-Stepper-Motor-Library/page3](https://forum.pjrc.com/threads/43491-New-Stepper-Motor-Library/page3)

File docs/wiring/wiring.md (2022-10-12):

# Schematics and electrical connections

The device is controlled using a custom PCB which connects the Teensy 3.5 development board with the DM542 stepper motor driver. The board is supplied at 24V and voltage regulators provide a 5V power supply to the Teensy board. In addition, there are two bi-directional logic level shifters (5-3.3V), so up to eight 5V signals can be converted to 3.3V. Connections include two BNC connectors to the Teensy DACs, SPI pins (3.3V) and some extra digital pins at 3.3V.  

|  |
|:--:|
| *Figure 1. PCB description* |

|  |
|:--:|
| *Figure 2. PCB with components soldered* |

A simplified version of the connections of the setup is shown in Figure 3:

|  |
|:--:|
| *Figure 3. Setup connections* |

The emergency stop opens the 24V power supply circuit. The whole experimental device is disconnected if pressed.

!!! warning
    Before soldering the Emergency stop pins check the continuity between and the logic operation between pins. If the button is pressed, the circuit must be open.

|  |
|:--:|
| *Figure 4. Emergency stop connections* |

## Bill of materials
|                Component                	| Quantity 	|       Supplier      	|                                                                                Reference                                                                                	|
|---------------------------------------	|--------	|-------------------	|-----------------------------------------------------------------------------------------------------------------------------------------------------------------------	 |
| PCB                                     	|    1     	|    -                	| [Gerber files](files/Gerber%20files.zip)                                                                                                            				         |
|    Logic Level Converter Module         	|    2     	|    Amazon           	| [link](https://www.amazon.co.uk/gp/product/B0148BLZGE/ref=ppx_yo_dt_b_asin_title_o05_s00)                                                                 	|
|    Teensy 3.5 microcontroller          	|    1     	|    PJRC             	|    [link](https://www.pjrc.com/store/teensy35.html)                                                                                                                             	|
|    BNC connectors                       	|    2     	|    RS Components    	|    [link](https://uk.rs-online.com/web/p/coaxial-connectors/7100453/)                                                                                                           	|
|    12V voltage regulator L7812CV        	|    1     	|    RS Components    	|    [link](https://uk.rs-online.com/web/p/linear-voltage-regulators/7931355/)                                                                                                    	|
|    5V voltage regulator LM7805          	|    1     	|    RS Components    	|    [link](https://uk.rs-online.com/web/p/linear-voltage-regulators/7968060/)                                                                                                   	|
|    Electrolytic capacitor 330 μF 25V    	|    1     	|    Ebay             	|    [link](https://www.ebay.co.uk/c/16029438608?iid=303554359855)                                                                                                                	|
|    Electrolytic capacitor 47 μF 50V      	|    1     	|    Ebay             	|    [link](https://www.ebay.co.uk/c/16029438608?iid=303554359855)                                                                                                                	|
|    Electrolytic capacitor 1 μF 50V       	|    1     	|    Ebay             	|    [link](https://www.ebay.co.uk/c/16029438608?iid=303554359855)                                                                                                                	|
|    Ceramic capacitor 100 nF 25V         	|    2     	|    RS Components    	|    [link](https://uk.rs-online.com/web/p/mlccs-multilayer-ceramic-capacitors/5381203/)                                                                                          	|
|    Ceramic capacitor 330 nF 25V         	|    2     	|    RS Components    	|    [link](https://uk.rs-online.com/web/p/mlccs-multilayer-ceramic-capacitors/1726542/)                                                                                          	|
|    Standard female pin headers          	| 6        	|    Amazon           	|    [link](https://www.amazon.co.uk/Aussel-Pieces-Breakaway-Connector-Arduino-PIN-2-20PCS/dp/B01M69EA9O/ref=sr_1_3)    	|
|    Emergency stop                       	|    1     	|    RS Components    	| [link](https://uk.rs-online.com/web/p/emergency-stop-push-buttons/4774890)                                                                                                         |
| Hall efect sensor                       	|    1     	|    Amazon           	| [link](https://www.amazon.co.uk/gp/product/B06XHG9CYN/ref=ppx_yo_dt_b_asin_title_o07_s00)                                                                     	|

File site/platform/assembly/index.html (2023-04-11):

- Docs »
- Main platform »
- Assembly

# Assembly instructions

Start assembling the Acrylic laser cut part “Base” with the Thorlabs RS05P pedestal posts and CF175 clamping forks using M6 screws. These posts are used to attach the rotary stage to the experimental table.



Figure 1. Base assembly

Use two M6 screws and nuts to attach the tube guide for the compressed air tube. Attach with M6 screws the two Thorlabs posts PH_50 and the TR_50 to the base.



Figure 2. Rotary joint telescopic posts assembly

The two Thorlabs PH_50 with the TR_50 are used to hold the rotary joint. To attach the rotary joint, you need two M6 or two M4 bolts with washers, depending on the position of the TR_50 (on one side is M4, on the other is M6). The compressed air tube can be installed now or at the end of the assembly.



Figure 3. Rotary joint assembly

Attach the seven Thorlabs RS150 posts to the base using M6 screws.



Figure 4. Thorlabs RS150 assembly

The animation below shows the order and location of components used for the base assembly.

Gif 1

Base Assembly

Once the rotary joint spacer is 3D printed, insert M3 brass threaded inserts and cure the part with UV light.



Figure 5. Rotary joint spacer threaded inserts

The Rotary Joint spacer is assembled with the rotary joint using 25 mm length M3 grab-screws. These are inserted using the radial holes on the bottom of the part.



Figure 6. Rotary joint spacer assembly



Figure 7. Rotary joint assembly

The crossed roller bearing BRS RU124X must be assembled with Platform 2 using ten M5 bolts and M5 nuts.



Figure 8. Crossed roller bearing assembled with the Platform 2

The manufacturer recommends the following installation order:



Figure 9. Crossed roller bearing installation method (left) and Cross roller bearing installed (right)

Warning

On the laser cut part “Platform 2”, it is recommended to drill chamfers for the M4 countersunk screws that will hold the motor. This step is important because the head of the screws has to be at the same level as the surface of Platform 2. Otherwise, they might touch the pulley or the belt.



Figure 10. Detail of the countersink screws level with the surface

Insert the four M4 screws with their nuts to fix the Nema 23 stepper motor to the Platform 2.



Figure 11. Motor assembly

The big pulley can be laser cut, as shown in Figure 12. It is composed by six layers of acrylic (2 x layer 1 in 5 mm thickness, 1 x layer 2 in 5 mm thickness, 2 x layer 2 in 3 mm thickness and 1 x layer 3 in 3 mm thickness). We recommend heating the threaded inserts with the soldering iron when inserting until they melt the plastic and go through the different layers. It is recommended to insert a couple using the external thread to get good alignment of the pulley teeth. Alternatively, there is an STL file to 3D print the pulley in one piece (this option has not been tested).



Figure 12. Big pulley assembly (left) and threaded inserts (right)

After laser cutting the circular platform, glue a small 5 mm Neodymium magnet as indicated in Figure 13. One of the magnet surfaces has to be coincident with the bottom surface of the platform. The magnet is there to interact with the Hall effect sensor at the bottom and trigger a state change to complete the homing position. Drilling chamfers on the outside holes for the countersunk screws, as seen in Figure 13, is also essential.



Figure 13. Magnet glueing and chamfers

Insert eight M6 screws to attach the Circular platform with the big pulley using the threaded inserts previously installed.



Figure 14. Circular platform and big pulley assembly

Assemble the Base with Platform 2 using 7 M6 screws.



Figure 15. Base and Platform 2 assembly

The animation below shows the order and location of components used for the platform assembly.

Gif2

Platform assembly

Assemble the Hall Effect sensor used for the homing sequence, using two M3 screws, two Hall effect spacers and the Hall Effect holder.



Figure 16. Hall Effect sensor assembly



Figure 17. Hall effect sensor placement

To assemble the circular platform, place the platform spacer on the inner ring of the bearing, then place the circular platform (assembled previously with the big pulley) on the spacer and use the M5 screws also installed as in the first step of the bearing (Figure 18).



Figure 18. Circular platform assembly

The animation below shows the order and location of components used for the big pulley assembly.

Gif3

Big pulley assembly

Next, use the Thorlabs PH_50 and the TR_50 posts to adjust the height of the rotary joint spacer until it makes contact with the circular platform surface (Figure 19). Now you can insert six M4 screws to secure it.



Figure 19. Adjustment of the Rotary joint height

The shaft of the Motor is 8 mm in diameter, and the inner diameter of the small pulley (https://uk.rs-online.com/web/p/belt-pulleys/1465412/) is 6 mm. The inner diameter of the pulley has to be increased to 8 mm with a vertical drill or milling machine (Figure 20). Add a second hole with a 3.3 mm diameter (using a 3.3 mm drill bit) to add a fixing screw that prevents the pulley from rotating around the motor shaft. Thread the hole using an M4 tap toolkit. For this step, a vice is recommended to hold the pulley while drilling. To connect the encoder shaft with the pulley, the encoder attachment must be 3D printed, and two extra 2.5 mm holes must be drilled at the top of the pulley. Then, an M3 thread must be made using the M3 tap tool.



Figure 20. Small pulley

The pulley can be assembled before or after attaching the motor to platform 2.



Figure 21. Small pulley and encoder

The belt must envelop the small pulley when you put it on the motor shaft. You will feel a high tension when pulling the belt since it is rigid.

Warning

Remember to put the flat part of the motor shaft oriented in a comfortable position to secure with the small pulley M4 screw afterwards.



Figure 22. Small pulley with motor shaft assembly

Three M3 screws are used to attach the Encoder holder to the encoder.



Figure 23. Encoder holder and encoder assembly

Once the belt cover part is laser cut, four brass M4 threaded inserts must be inserted into the holes by heating them with the soldering iron or applying pressure.



Figure 24. M4 threaded inserts on the belt cover

Now four M4 screws can be inserted from the top placing the encoder spacers coincident with the holes.



Figure 25. M4 threaded inserts on the belt cover

The belt cover can now be installed using M6 screws, nuts and the cover spacers. After that, the encoder shaft must be in contact with the M4 grub screw at the top of the pulley.



Figure 26. Belt cover assembly

The animation below shows the order and location of components used for the small pulley assembly.

Gif3

Small pulley assembly

To regulate the belt's tension, two ball bearings are inserted on the belt tensor, and one M6 screw is used to install it in the guide. Use four washers to get a good fit on the inside and outside of the screw with the two sides of the belt cover and Platform 2.



Figure 27. Belt tensor assembly



Figure 28. Detail of the two ball bearings

Now adjust the tension of the belt. Check the belt is not touching the bottom or the top surfaces.



Figure 29. Space on both sides of the belt

The vertical tubing for compressed air can now be inserted through the rotary joint through-hole into the pneumatic tube elbow. Lastly, the sphere holder has to be attached with four M6 screws.





Figure 30-31. Sphere holder assembly



Figure 32. Complete assembly

Next Previous

Built with MkDocs (https://www.mkdocs.org/) using a theme (https://github.com/snide/sphinx_rtd_theme) provided by Read the Docs (https://readthedocs.org).

« Previous Next »

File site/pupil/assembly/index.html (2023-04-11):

- Docs »
- Pupil Camera »
- Assembly

# Assembly instructions

- Cut 2 pieces of silicone tube to similar lengths as the mirror edges (36 mm and 25 mm).
- Glue both parts into the mirror holder.
- Use a scalpel to make a longitudinal cut along both tubes.
- Insert a 6 mm diameter Thorlabs post into the mirror holder.



Figure 1. Mirror holder assembly

- Use a 3D printing material with opaque features (e.g. FormLabs black resin). If using clear resin, use black matt spray to block out external light.
- Use 4 M2 screws and nuts to attach the camera to the camera holder.
- Insert the filter, mounted on a CP35/M and an SM1L03 lens tube in the filter holder. Use 4 M3 screws to attach it to the filter holder cover.
- Use two long (25-30 mm) M3 screws as shafts to open and close the filter holder.



Figure 2. Camera and filter holder assembly

- Use an M6 screw and nut to attach the camera holder to the MT1/M linker with the camera holder lip found in the "Instrument ring and head holder" section.



Figure 3. Camera assembly to head-fixation system

- Attach the mirror holder to the instrument ring or the rotation platform using Thorlabs components (e.g. RA90TR/M and 12.7 mm post).
- Mount the head fixation system onto the instrument ring.



Figure 4. Camera and mirror

Next Previous

Built with MkDocs (https://www.mkdocs.org/) using a theme (https://github.com/snide/sphinx_rtd_theme) provided by Read the Docs (https://readthedocs.org).

« Previous Next »

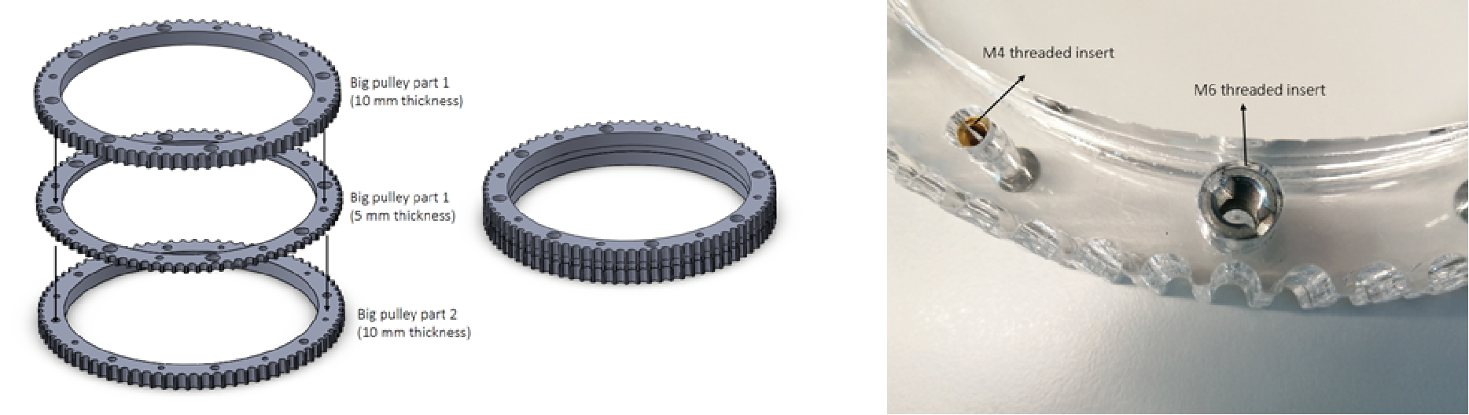
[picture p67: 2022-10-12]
docs/platform/img/pulley_assembly.png

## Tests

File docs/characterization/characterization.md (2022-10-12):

Terminology and measurements in this section follow [this document](https://www.newport.com/n/motion-basics-terminology-and-standards). 
Users should conduct their own characterization with the specific platform weights and weight distributions. 

The rotary stage's accuracy and repeatability have been evaluated by recording the angle (°) of the incremental encoder (2400 pulses per revolution) and the angle obtained from the teensystep step counter simultaneously. Figure 1 shows an example test of the stage performance, in this case without the load of the head holder. The stage is repeatedly sent to the set point positions (0 and 360 degrees). The final positions are highly accurate (360.06 ± 0.11° and 0.04 ± 0.07°), suggesting little error accumulation. 

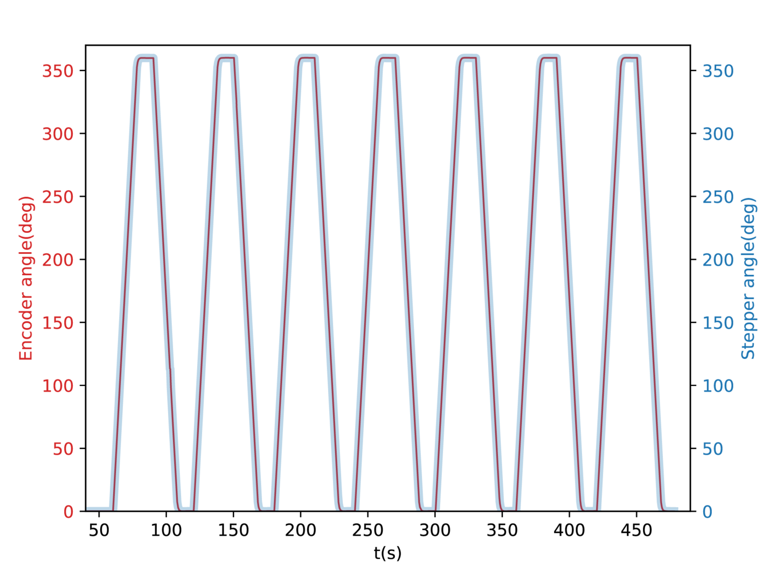
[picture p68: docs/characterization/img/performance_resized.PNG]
|  |
|:--:|
| *Figure 1. Rotary stage performance* |

Data and code for this characterization are available [here](data/rotary_stage_validation/Closed%20loop%20without%20load/closed_loop_without_load.zip).

## Minimum incremental motion (MIM) and backlash
The minimum incremental motion reliably measured corresponds to 0.1 degrees. The backlash, in the worst-case scenario corresponding to the offset created by the change in direction of the MIM tests, has been 0.04 degrees.

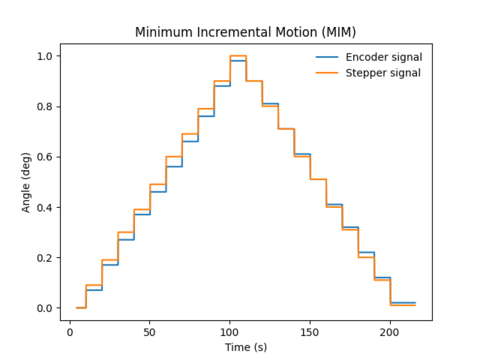
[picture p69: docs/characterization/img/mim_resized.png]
|  |
|:--:|
| *Figure 2. Minimum incremental motion measurement* |

Data and code for this characterization are available [here](data/rotary_stage_validation/Minimum%20incremental%20motion%20(MIM)/MIM.zip).

## Accuracy and repeatability
In order to evaluate the accuracy and repeatability of the rotary stage, a sequence of increments of 45 degrees in both rotation directions has been performed, collecting 8 position deviations in each direction (16 per each velocity/acceleration condition). The overall accuracy and repeatability have been calculated from all conditions according to the following equations:

Accuracy:
equation1

Repeatability:
equation2

Where x<sub>i</sub> and s<sub>i</sub> are the average inaccuracy and the standard deviation, respectively, at position i. Up and down arrows represent the positive and negative directions. 

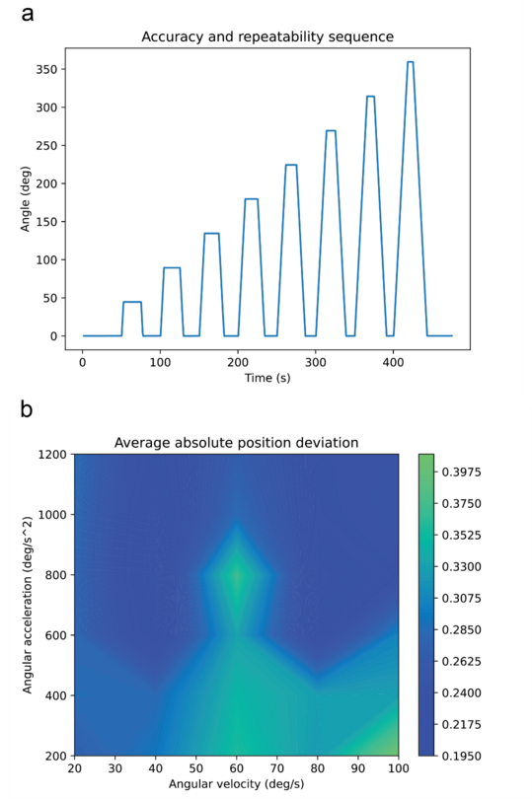
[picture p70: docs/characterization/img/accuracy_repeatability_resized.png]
|  |
|:--:|
| *Figure 3. Accuracy and repeatability test sequence (a) and*|
| *average of absolute position deviation in every angular velocity and acceleration condition (b)* |

## Closed-loop characterization

For the closed loop algorithm, the stability of the system response has been evaluated by the analysis of the step response for all previously described conditions (20-100 °·s¯¹ and 200-1200 °·s¯²). A contour plot has been extracted to be used as a map to avoid regions of inaccuracy and instability. Sometimes even achieving a small error the stage can overshoot as shown in Figure 4 (right). 

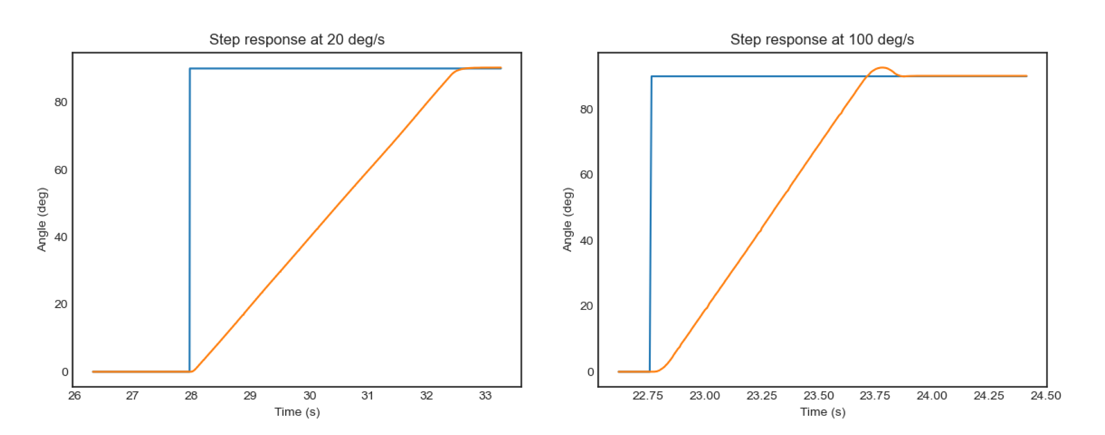
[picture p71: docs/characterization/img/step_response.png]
|  |
|:--:|
| *Figure 4. Example step functions (0-90°) at different velocity and acceleration values.*|
| *(left) 20 °·s¯¹, 200 °·s¯². (right) 100 °·s¯¹, 1200 °·s¯².*| 

Figures 5 highlight regions in red to avoid errors and instability around the setpoint. 

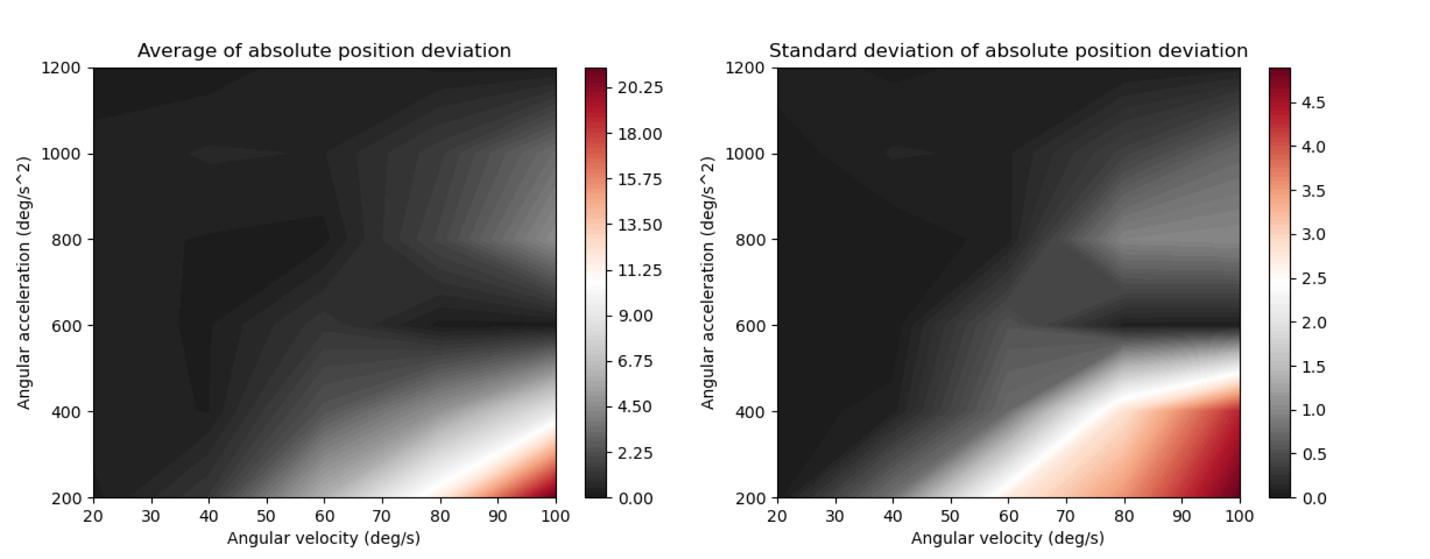
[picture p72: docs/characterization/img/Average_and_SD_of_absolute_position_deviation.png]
|  |
|:--:|
| *Figure 5. Average (left) and standard deviation (right) of the absolute position deviation.* |

Data and code for this characterization are available [here](data/rotary_stage_validation/Closed%20loop/closed_loop.zip).

# Specifications and characterization of the rotary stage

| parameter					         	| value	|
|--------------------------------------	|--------	|
| Resolution stepper motor (°)         	| 0.0024 	|
| Resolution of the encoder (°)       	| 0.024  	|
| Accuracy (°)                         	| 0.37   	|
| Repeatability (°)                    	| 0.1    	|
| Minimum incremental motion (°)       	| 0.1    	|
| Maximum angular velocity (°·s¯¹)     	| 100    	|
| Maximum angular acceleration (°·s¯²) 	| 1200   	|
| Backlash (°)                         	| 0.04   	|

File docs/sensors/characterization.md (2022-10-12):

# Sensor characterization

The library to interface with the sensors is available on GitHub [[1]](#references). It provides access to the SQUAL register, which gives the reading of how good is the surface pattern to detect xy displacements. Figure 1 shows the measurement error vs the SQUAL value for one revolution of the sphere. The maximum SQUAL value was 120 (0 means no surface detection).

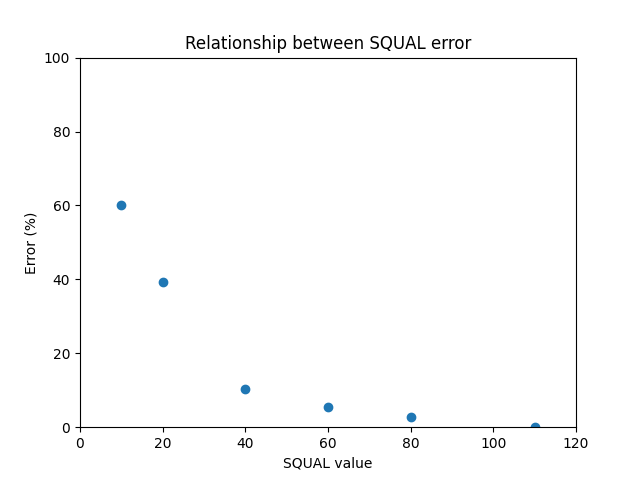
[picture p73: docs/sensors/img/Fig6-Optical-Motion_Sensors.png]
|  |
|:--:|
| *Figure 1. Relationship between the measurement error and the SQUAL value* |

## Characterization

The characterization of the ADNS2610 optical sensors was performed by collecting 30 revolutions of the polystyrene sphere. The number of the optical sensor internal units per revolution was 9391 on average. The polystyrene sphere has a perimeter of 61.86 cm, thus, the number of sensor internal units per cm equals 151.81.

SQUAL values were recorded simultaneously (average 82.56 ± 23.92). Figure 2 (left) shows the distribution of the SQUAL values. Figure 2 (right) shows the relationship between the rotation speed as the increment in sensor internal units between two samples and the SQUAL value. 

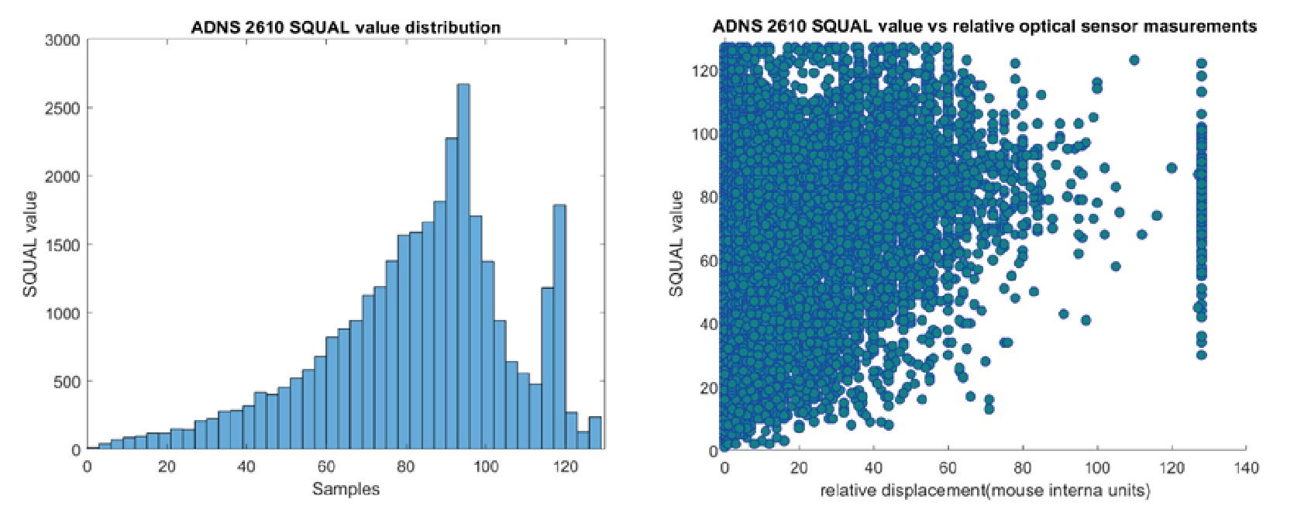
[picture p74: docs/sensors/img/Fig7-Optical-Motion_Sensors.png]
|  |
|:--:|
| *Figure 2. Distribution of the SQUAL values (left). Speed vs SQUAL value relationship (right)* |

## Adjustments

The vertical and horizontal positions of the sensor should be adjusted. The vertical position can be adjusted by the Thorlab post for the sensor to match the sphere's equator. Then the horizontal position can be optimized by adjusting the sensor holder until a SQUAL value higher than 100 has been achieved.

## Data
The data and code used for the sensor validation are available [here](../characterization/data/ADNS_2610_validation/ADNS_2610_validation.zip).

# References
[1] [https://github.com/zapmaker/OptiMouse](https://github.com/zapmaker/OptiMouse)

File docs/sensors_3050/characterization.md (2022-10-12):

# Characterization

Before calibration, the position of the sensor must be adjusted to align with the sphere's equator vertically. Then the horizontal position can be adjusted until a SQUAL value of approximately 50 is achieved.
Several recordings of 5 seconds at 1000 Hz were performed to characterize the perimeter measured by the sensor and establish the relationship between the actual and measured perimeter. Two sensors were used, and separate recordings were made rotating the sphere around the yaw and roll axes (Figure 1).

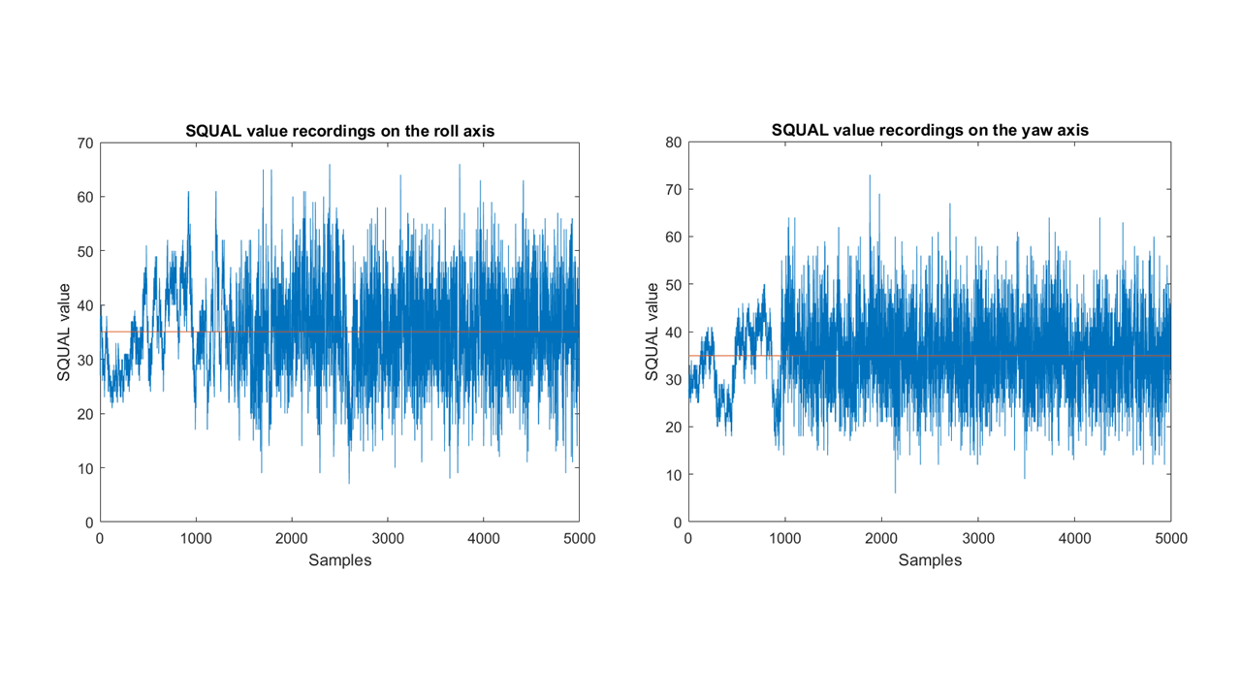
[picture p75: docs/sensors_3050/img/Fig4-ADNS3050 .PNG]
|  |
|:--:|
| *Figure 1. SQUAL value recordings for both axes* |

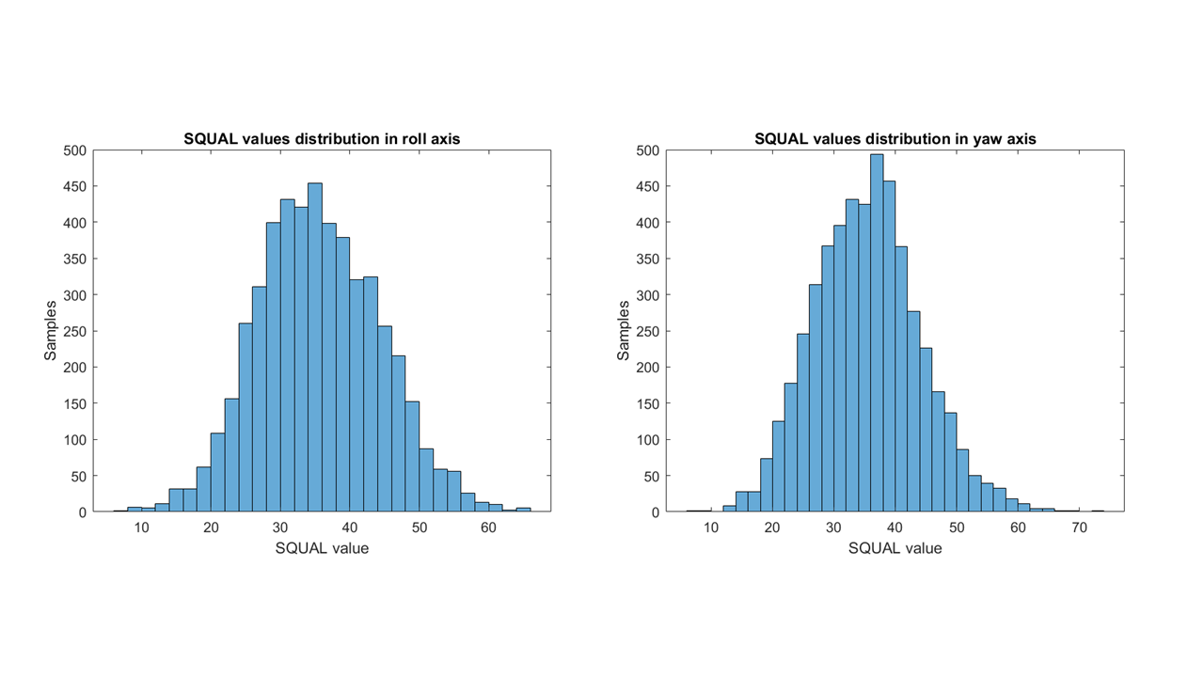
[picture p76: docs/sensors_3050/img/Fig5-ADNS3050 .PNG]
|  |
|:--:|
| *Figure 2. Distribution of the SQUAL values on each axis* |

The results show a homogeneous distribution of the SQUAL value depending on the relative distance change (Figure 3).

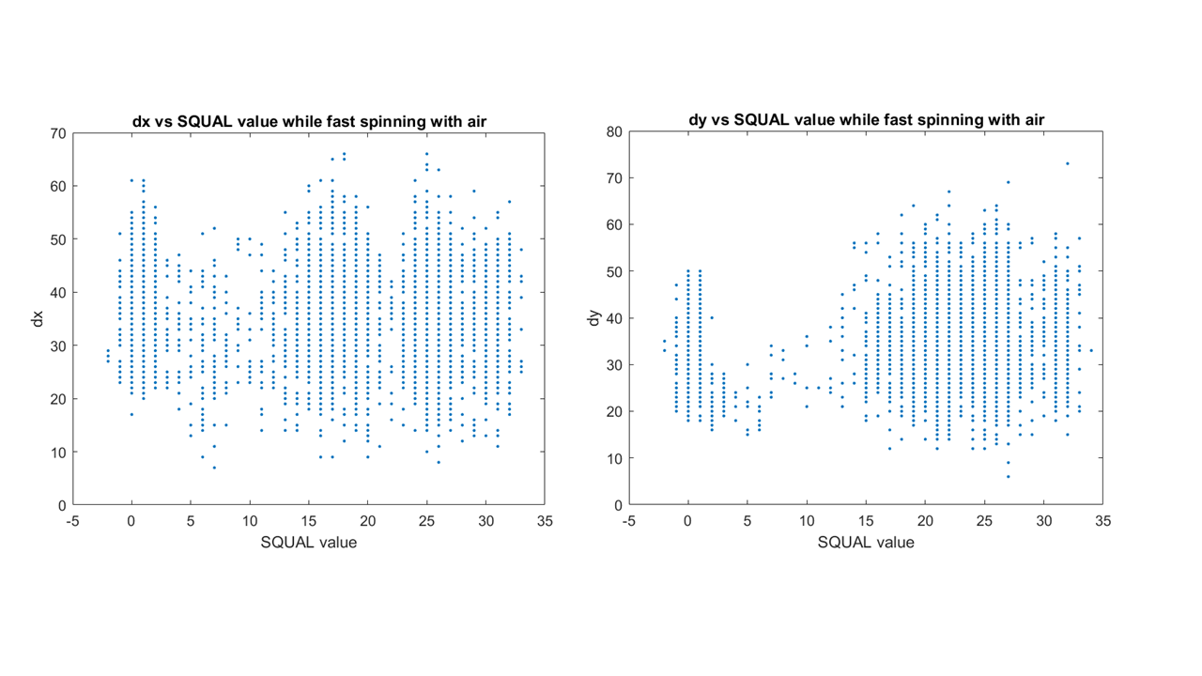
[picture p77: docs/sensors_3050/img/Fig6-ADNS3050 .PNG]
|  |
|:--:|
| *Figure 3. Relationship between relative displacements and the SQUAL value* |

The calibration was performed by repeating several measurements of one revolution for the roll and yaw axes (n = 6 and n = 5, respectively). For each recording, the sphere has been rotated by hand for one revolution using an external mark. 

|  |
|:--:|
| *Figure 4. Recordings of absolute displacements in roll and yaw axes of one revolution* | 

As shown in Figure 4, for both axes the recordings converge towards a final value. The conversion factor between mouse internal units and sphere displacement is the average of this absolute final value for both axes (n = 11). The average was 21,966 for the roll axis and 20,109 mouse internal units for the yaw axis, giving a final average of 21,038 mouse internal units for a perimeter of 61.89 cm, hence a conversion factor of 339.92 mouse internal units per cm.

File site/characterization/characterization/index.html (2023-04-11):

- Docs »
- Characterization and software »
- Platform characterization

Terminology and measurements in this section follow this document (https://www.newport.com/n/motion-basics-terminology-and-standards). Users should conduct their own characterization with the specific platform weights and weight distributions.

The rotary stage's accuracy and repeatability have been evaluated by recording the angle (°) of the incremental encoder (2400 pulses per revolution) and the angle obtained from the teensystep step counter simultaneously. Figure 1 shows an example test of the stage performance, in this case without the load of the head holder. The stage is repeatedly sent to the set point positions (0 and 360 degrees). The final positions are highly accurate (360.06 ± 0.11° and 0.04 ± 0.07°), suggesting little error accumulation.



Figure 1. Rotary stage performance

Data and code for this characterization are available here.

## Minimum incremental motion (MIM) and backlash

The minimum incremental motion reliably measured corresponds to 0.1 degrees. The backlash, in the worst-case scenario corresponding to the offset created by the change in direction of the MIM tests, has been 0.04 degrees.



Figure 2. Minimum incremental motion measurement

Data and code for this characterization are available here.

## Accuracy and repeatability

In order to evaluate the accuracy and repeatability of the rotary stage, a sequence of increments of 45 degrees in both rotation directions has been performed, collecting 8 position deviations in each direction (16 per each velocity/acceleration condition). The overall accuracy and repeatability have been calculated from all conditions according to the following equations:

Accuracy: equation1

Repeatability: equation2

Where xi and si are the average inaccuracy and the standard deviation, respectively, at position i. Up and down arrows represent the positive and negative directions.



Figure 3. Accuracy and repeatability test sequence (a) and

average of absolute position deviation in every angular velocity and acceleration condition (b)

## Closed-loop characterization

For the closed loop algorithm, the stability of the system response has been evaluated by the analysis of the step response for all previously described conditions (20-100 °·s¯¹ and 200-1200 °·s¯²). A contour plot has been extracted to be used as a map to avoid regions of inaccuracy and instability. Sometimes even achieving a small error the stage can overshoot as shown in Figure 4 (right).



Figure 4. Example step functions (0-90°) at different velocity and acceleration values.

(left) 20 °·s¯¹, 200 °·s¯². (right) 100 °·s¯¹, 1200 °·s¯².

Figures 5 highlight regions in red to avoid errors and instability around the setpoint.



Figure 5. Average (left) and standard deviation (right) of the absolute position deviation.

Data and code for this characterization are available here.

# Specifications and characterization of the rotary stage

parameter | value
Resolution stepper motor (°) | 0.0024
Resolution of the encoder (°) | 0.024
Accuracy (°) | 0.37
Repeatability (°) | 0.1
Minimum incremental motion (°) | 0.1
Maximum angular velocity (°·s¯¹) | 100
Maximum angular acceleration (°·s¯²) | 1200
Backlash (°) | 0.04

Next Previous

Built with MkDocs (https://www.mkdocs.org/) using a theme (https://github.com/snide/sphinx_rtd_theme) provided by Read the Docs (https://readthedocs.org).

« Previous Next »

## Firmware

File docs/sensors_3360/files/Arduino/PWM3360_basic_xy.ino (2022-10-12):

#include <PMW3360.h>
#include <elapsedMillis.h>


#define SS  10   // Slave Select pin. Connect this to SS on the module.
elapsedMillis timer;

boolean surface_quality = 0;

#define Motion  0x02
#define Delta_X_L 0x03
#define Delta_X_H 0x04
#define Delta_Y_L 0x05
#define Delta_Y_H 0x06
#define SQUAL 0x07

PMW3360 sensor;

int sumx = 0;
int sumy = 0;
int squal;

void setup() {
  Serial.begin(9600);  
  while(!Serial);
  
  //sensor.begin(10, 1600); // to set CPI (Count per Inch), pass it as the second parameter
  if(sensor.begin(SS))  // 10 is the pin connected to SS of the module.
    Serial.println("Sensor initialization successed");
  else
    Serial.println("Sensor initialization failed");
  
  //sensor.setCPI(1600);    // or, you can set CPI later by calling setCPI();
}

void loop() 
{

  PMW3360_DATA data = sensor.readBurst();

  int xh = sensor.readReg(Delta_X_H);
  int xl = sensor.readReg(Delta_X_L);
  int xh_2 = xh<<8;
  int x = convTwosComp(xh|xl);
  
  sumx += x;

  int yh = sensor.readReg(Delta_Y_H);
  int yl = sensor.readReg(Delta_Y_L);
  int yh_2 = yh<<8;
  int y = convTwosComp(yh|yl);
  sumy += y;
  
  squal = convTwosComp(sensor.readReg(SQUAL));

  //  sumx += convTwosComp(sensor.readReg(Delta_X_L));
  
  if (timer > 20)
  {
  
    if (surface_quality == 1)
    {
      Serial.println(squal);
      timer = 0;
    }
    else
    {
      Serial.print(sumx);
      Serial.print("\t");
      Serial.println(sumy);
      timer = 0;
    }
  }
  
  //Serial.println(convTwosComp(sensor.readReg(0x03)));
//  if(data.isOnSurface && data.isMotion)
//  {
//    Serial.print(data.dx);
//    Serial.print("\t");
//    Serial.print(data.dy);
//    Serial.println();
//  }
  
  //delay(10);
}

int convTwosComp(int b)
{
  //Convert from 2's complement
  if(b & 0x80)
  {
    b = -1 * ((b ^ 0xff) + 1);
  }
  return b;
}  

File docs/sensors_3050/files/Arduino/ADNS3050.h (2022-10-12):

#include <SPI.h>

 // SPI and misc pins for the ADNS 1
 #define PIN_SCLK   SCK
 #define PIN_MISO   MISO
 #define PIN_MOSI   MOSI
 #define PIN_NCS    7
 #define PIN_MOTION 5     // Not used

  // SPI and misc pins for the ADNS 2
 #define PIN_SCLK2   SCK
 #define PIN_MISO2   MISO
 #define PIN_MOSI2   MOSI
 #define PIN_NCS2    6
 #define PIN_MOTION2 8  // Not used
  
// Define all the registers
 #define PROD_ID                          0x00
 #define REV_ID                           0x01
 #define MOTION_ST                        0x02
 #define DELTA_X                          0x03
 #define DELTA_Y                          0x04
 #define SQUAL                            0x05
 #define SHUT_HI                          0x06
 #define SHUT_LO                          0x07
 #define PIX_MAX                          0x08
 #define PIX_ACCUM                        0x09
 #define PIX_MIN                          0x0a
 #define PIX_GRAB                         0x0b
 #define MOUSE_CTRL                       0x0d
 #define RUN_DOWNSHIFT                    0x0e
 #define REST1_PERIOD                     0x0f
 #define REST1_DOWNSHIFT                  0x10
 #define REST2_PERIOD                     0x11
 #define REST2_DOWNSHIFT                  0x12
 #define REST3_PERIOD                     0x13
 #define PREFLASH_RUN                     0x14
 #define PREFLASH_RUN_DARK                0x18
 #define MOTION_EXT                       0x1b
 #define SHUT_THR                         0x1c
 #define SQUAL_THRESHOLD                  0x1d
 #define NAV_CTRL2                        0x22
 #define MISC_SETTINGS                    0x25
 #define RESOLUTION                       0x33
 #define LED_PRECHARGE                    0x34
 #define FRAME_IDLE                       0x35
 #define RESET                            0x3a
 #define INV_REV_ID                       0x3f
 #define LED_CTRL                         0x40
 #define MOTION_CTRL                      0x41
 #define AUTO_LED_CONTROL                 0x43
 #define REST_MODE_CONFIG                 0x45


void com_start()
{
  // Start mouse 1
  digitalWrite(PIN_NCS, HIGH);
  delay(20);
  digitalWrite(PIN_NCS, LOW); 
  
  // Start mouse 2
  digitalWrite(PIN_NCS2, HIGH);
  delay(20);
  digitalWrite(PIN_NCS2, LOW);
}



byte Read(byte reg_addr){
  digitalWrite(PIN_NCS, LOW);//begin communication
  // send address of the register, with MSBit = 0 to say it's reading
  SPI.transfer(reg_addr & 0x7f );
  delayMicroseconds(100);
  // read data
  byte data = SPI.transfer(0);
  delayMicroseconds(30);
  digitalWrite(PIN_NCS, HIGH);//end communication
  delayMicroseconds(30);

  return data;
}


byte Read2(byte reg_addr){
  digitalWrite(PIN_NCS2, LOW);//begin communication
  // send address of the register, with MSBit = 0 to say it's reading
  SPI.transfer(reg_addr & 0x7f );
  delayMicroseconds(100);
  // read data
  byte data = SPI.transfer(0);
  delayMicroseconds(30);
  digitalWrite(PIN_NCS2, HIGH);//end communication
  delayMicroseconds(30);

  return data;
}

void Write(byte reg_addr, byte data){
  digitalWrite(PIN_NCS, LOW);
  //send address of the register, with MSBit = 1 to say it's writing
  SPI.transfer(reg_addr | 0x80 );
  //send data
  SPI.transfer(data);
  delayMicroseconds(30);
 digitalWrite(PIN_NCS, HIGH);//end communication
  delayMicroseconds(30);
}

void Write2(byte reg_addr, byte data){
  digitalWrite(PIN_NCS2, LOW);
  //send address of the register, with MSBit = 1 to say it's writing
  SPI.transfer(reg_addr | 0x80 );
  //send data
  SPI.transfer(data);
  delayMicroseconds(30);
 digitalWrite(PIN_NCS2, HIGH);//end communication
  delayMicroseconds(30);
}

void startup(){
  //--------Setup SPI Communication---------
  Serial.begin(115200);
  byte out = 0;
  byte read = 0;
  byte bit = 0;
  pinMode(PIN_MISO,INPUT);
  pinMode(PIN_NCS,OUTPUT);
  SPI.begin();
  // set the details of the communication
  SPI.setBitOrder(MSBFIRST); // transimission order of bits
  SPI.setDataMode(SPI_MODE3); // sampling on rising edge
  //SPI.setClockDivider(SPI_CLOCK_DIV16); // 16MHz/16 = 1MHz
  SPI.setClockDivider(21); //  on the due default 21 (84/21) 4 MHz
  delay(10);

  //----------------- Power Up and config ---------------
  com_start();
  Write(RESET, 0x5a); // force reset
  delay(100); // wait for it to reboot
  Write(MOUSE_CTRL, 0x20);//Setup Mouse Control
  Write(MOTION_CTRL, 0x00);//Clear Motion Control register
  delay(100);
  
//  Write(NAV_CTRL2, 0x80); // Register to change the awake mode 0 enabled / 1 disabled on the bit 7 (1000000)
//  delay(100);
//  Serial.println(Read(NAV_CTRL2),BIN);
//  delay(100);
//  Serial.println(Read(NAV_CTRL2),BIN);
//  delay(100);
    Write(AUTO_LED_CONTROL, 0x07); //register is used to control the LED operating mode and current to optimization the power consumption.
    //0x09 should be LED continous ON and 0x07 should be 20mA switching disabled
    delay(100);
    Write(LED_CTRL, 0x04);//(register st to disable auto_LED switching) required to operate the previous command if not it is ignored
    delay(100); 
    Serial.println(Read(AUTO_LED_CONTROL),HEX);
    delay(100);
    Serial.println(Read(LED_CTRL),HEX);
    delay(100);
  
  }

void startup2(){
  //--------Setup SPI Communication---------
  Serial.begin(115200);
  byte out = 0;
  byte read = 0;
  byte bit = 0;
  pinMode(PIN_MISO,INPUT);
  pinMode(PIN_NCS2,OUTPUT);
  SPI.begin();
  // set the details of the communication
  SPI.setBitOrder(MSBFIRST); // transimission order of bits
  SPI.setDataMode(SPI_MODE3); // sampling on rising edge
  //SPI.setClockDivider(SPI_CLOCK_DIV16); // 16MHz/16 = 1MHz
  SPI.setClockDivider(21); //  on the due default 21 (84/21) 4 MHz
  delay(10);

  //----------------- Power Up and config ---------------
  com_start();
  Write(RESET, 0x5a); // force reset
  delay(100); // wait for it to reboot
  Write(MOUSE_CTRL, 0x20);//Setup Mouse Control
  Write(MOTION_CTRL, 0x00);//Clear Motion Control register
  delay(100);
  //Write(AUTO_LED_CONTROL, 0x09);
  //Write(LED_CTRL, 0x04);
  }


int convTwosComp(int b){ //Convert from 2's complement
   if(b & 0x80){
     b = -1 * ((b ^ 0xff) + 1);
     }
   return b;
   }

void getXY(){//Prints out X and Y values to the serial terminal, use getX and getY sequentially for most operations
  byte x = 0;
  byte y = 0;
	 x= Read(0x03);
	    y = Read(0x04);
     Serial.println("x");
	     Serial.println(convTwosComp(x));
      Serial.println("y");
Serial.println(convTwosComp(y));
}


int getX(){//returns the X acceleration value
  byte x = 0;
  x= Read(0x03);
  return(convTwosComp(x));
}

int getY(){//returns the Y acceleration value
  byte y = 0;
  y= Read(0x04);
  return(convTwosComp(y));
}

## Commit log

2022-10-12 mkdocs gh-deploy
    [Hall Efect sensor Holder.stp, Hall Effect sensor spacer.STEP, Head_plate_holder_1.stp, Head_plate_holder_2.stl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]
2023-11-28 Added new pupil camera, lens and accessories
    [FFY-U3-50-R1.STEP]
2023-12-06 FCStd + STL + STEP
    [MT1L_linker.FCStd, MT1L_linker.step, MT1L_linker.stl, NPX_scope_holder.FCStd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]
